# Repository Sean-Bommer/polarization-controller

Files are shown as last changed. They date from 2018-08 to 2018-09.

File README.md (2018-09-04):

# polarization-controller-Unit
Repository for all the final files of the polarization controller project completed by Sean Bommer.

The polarization controller unit (PCU) is a modular laser cut device that is capable of rotating 2 1-inch polarizing waveplates.
it operates using an Arduino Nano and two DRV8834 stepper motor drivers, found at the folowing link.
https://www.pololu.com/product/2134
which control 2 28BYJ-48 5V Stepper Motors.
the construction is made up from 3mm acrylic and M3 bolts and nuts.

The PCU can be powered from the 5V line of the Arduino Nano, which allowing for the whole system to be run from the USB port of a PC.
The OS for the device is contained in the Arduino IDE code in this repository, two versions are available:
  
  The 'position' version sets the start location (it's position when switched on) as position = 0 Degrees and then rotates the waveplate     to  the target orientation with respect to this 0 position. For example, upon start up the device is asked to rotate to 90 degrees. the   device turns to this position. it is then asked to turn to 90 degrees again. the device does not move, as it is already at 90 degrees.
  
  The 'distance' version reads the degrees input as how far it should rotate. For example, upon start up the device is asked to rotate 90   degrees. the device turns this distance. it is then asked to turn 90 degrees again. the device will turn another 90 degrees, thus being   180 degrees from it's origin point.
  
This device is designed to be very modular, and complies to the dimensions required for the Thorlabs cage mount system. the waveplates are controlled independently of each other so it can operate with either one or 2 waveplates. 

When attached to the base mount via the M3 screws the, the whole system can be mounted to an optical breadboard via the 2 slots either side of the base and up to 4 L-shaped mounting brackets. In this configuration, with two waveplates setup, the PCU can serve as a mounting point for a simple optical cage setup as well.

FOLDERS:
        
        The Arduino folder contains the position and distance versions of the OS which are compatible with the arduino Nano.
        it also contains the autostep testscript, that can be used to check if all components work without serial communication and also 
        measure any motor drift the system has when used in conjunction with the Matlab findMotorDrift.m file.
        
        The Matlab folder has the findMotorDrift.m file which can be used to measure the motor drift of the system whn used with the
        autostep arduino script.
        
        The LabVIEW folder holds a simple Serial Interface with the PCU allowing simple click and go operation of the PCU

        The PCB folder has all the Kicad files needed for the design of the PCU PCB on a one-sided copper plate.

        the Fusion 360 contains the design files for the laser cut acrylic parts of the PCU.

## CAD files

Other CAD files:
Fusion360/Driver Gear (hobby) v5.f3d
Fusion360/Lens Holder Cover v5.f3d
Fusion360/Master Base Mount v6.f3d
Fusion360/Master Panels v19.f3d

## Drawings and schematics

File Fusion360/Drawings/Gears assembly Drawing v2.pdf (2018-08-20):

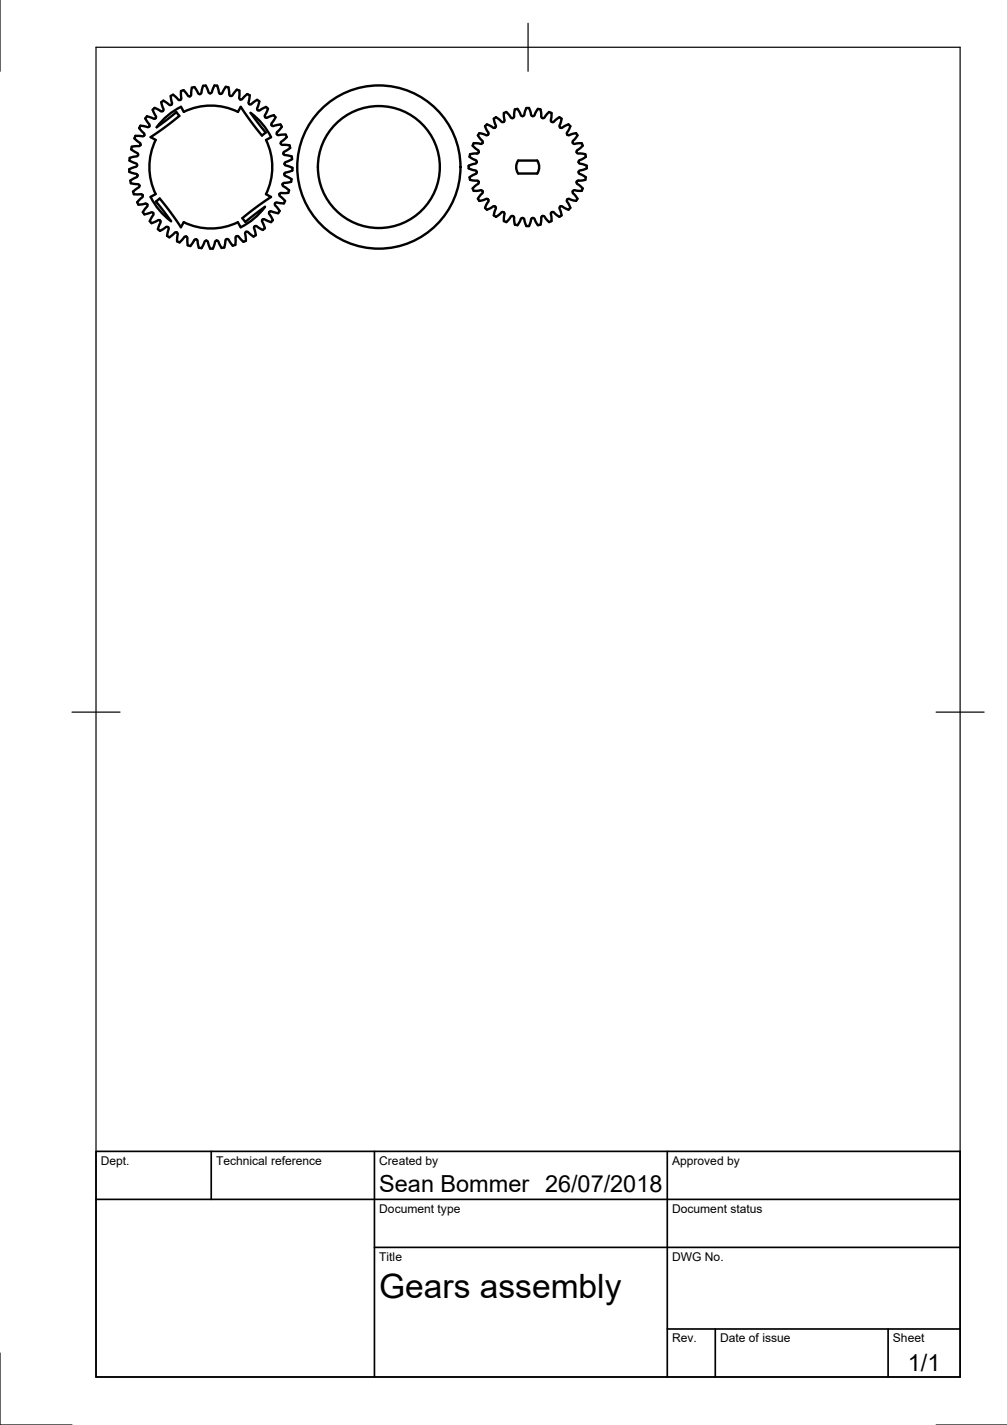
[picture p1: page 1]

Dept. | Technical reference | Created by Sean Bommer 26/07/2018 | Approved by

Document type | Document status

Title Gears assembly | DWG No.

Rev. | Date of issue | Sheet 1/1

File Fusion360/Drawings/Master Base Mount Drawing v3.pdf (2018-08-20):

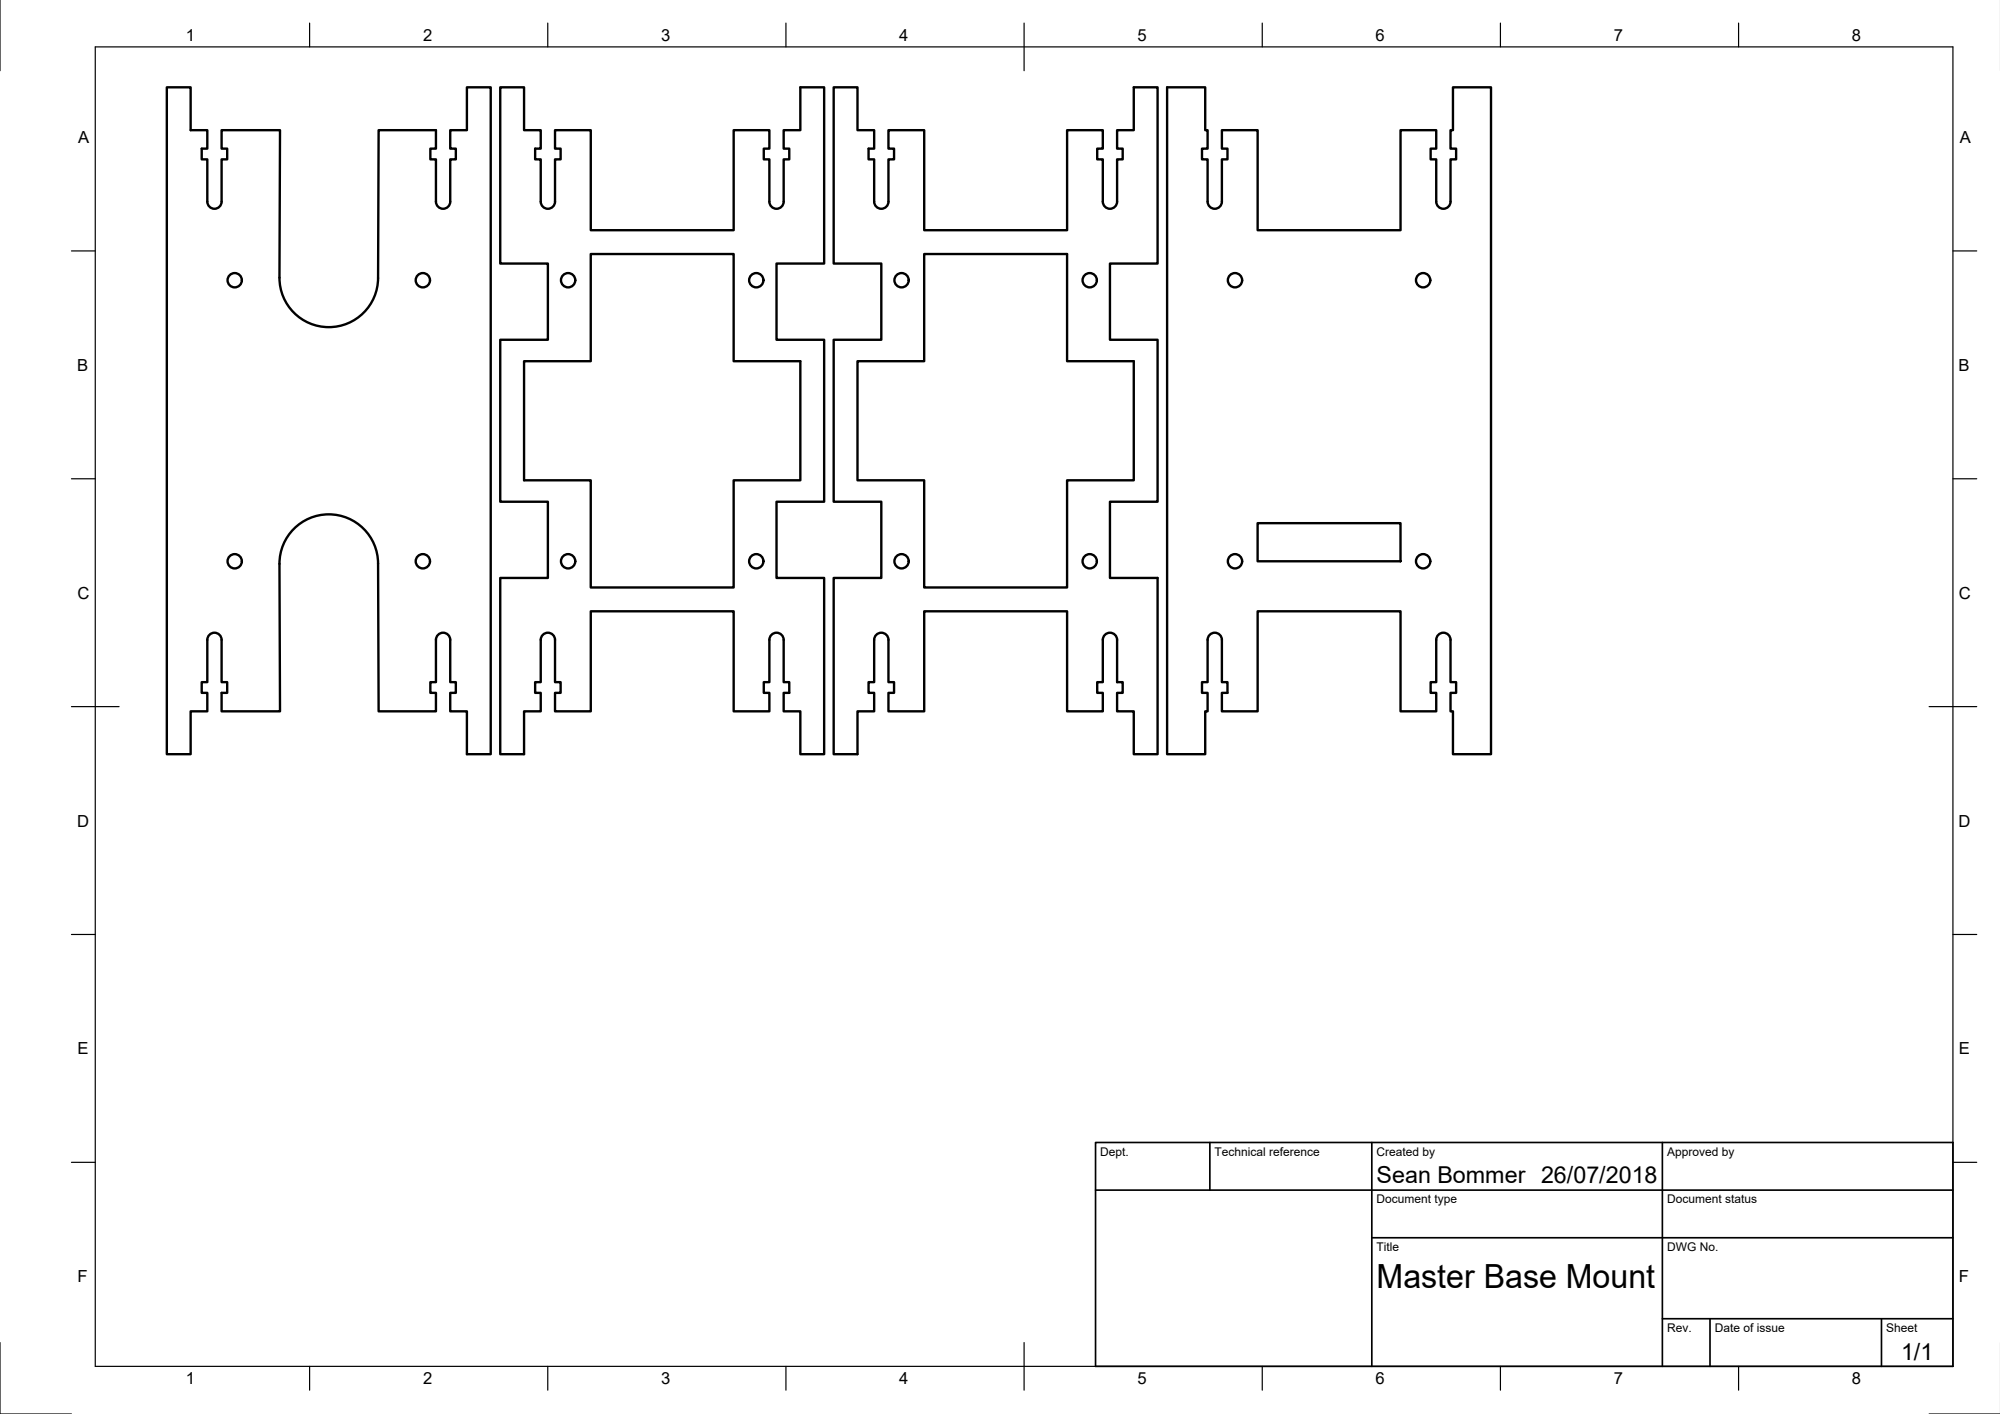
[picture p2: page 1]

Dept. | Technical reference | Created by Sean Bommer 26/07/2018 | Approved by

Document type | Document status

Title Master Base Mount | DWG No.

Rev. | Date of issue | Sheet 1/1

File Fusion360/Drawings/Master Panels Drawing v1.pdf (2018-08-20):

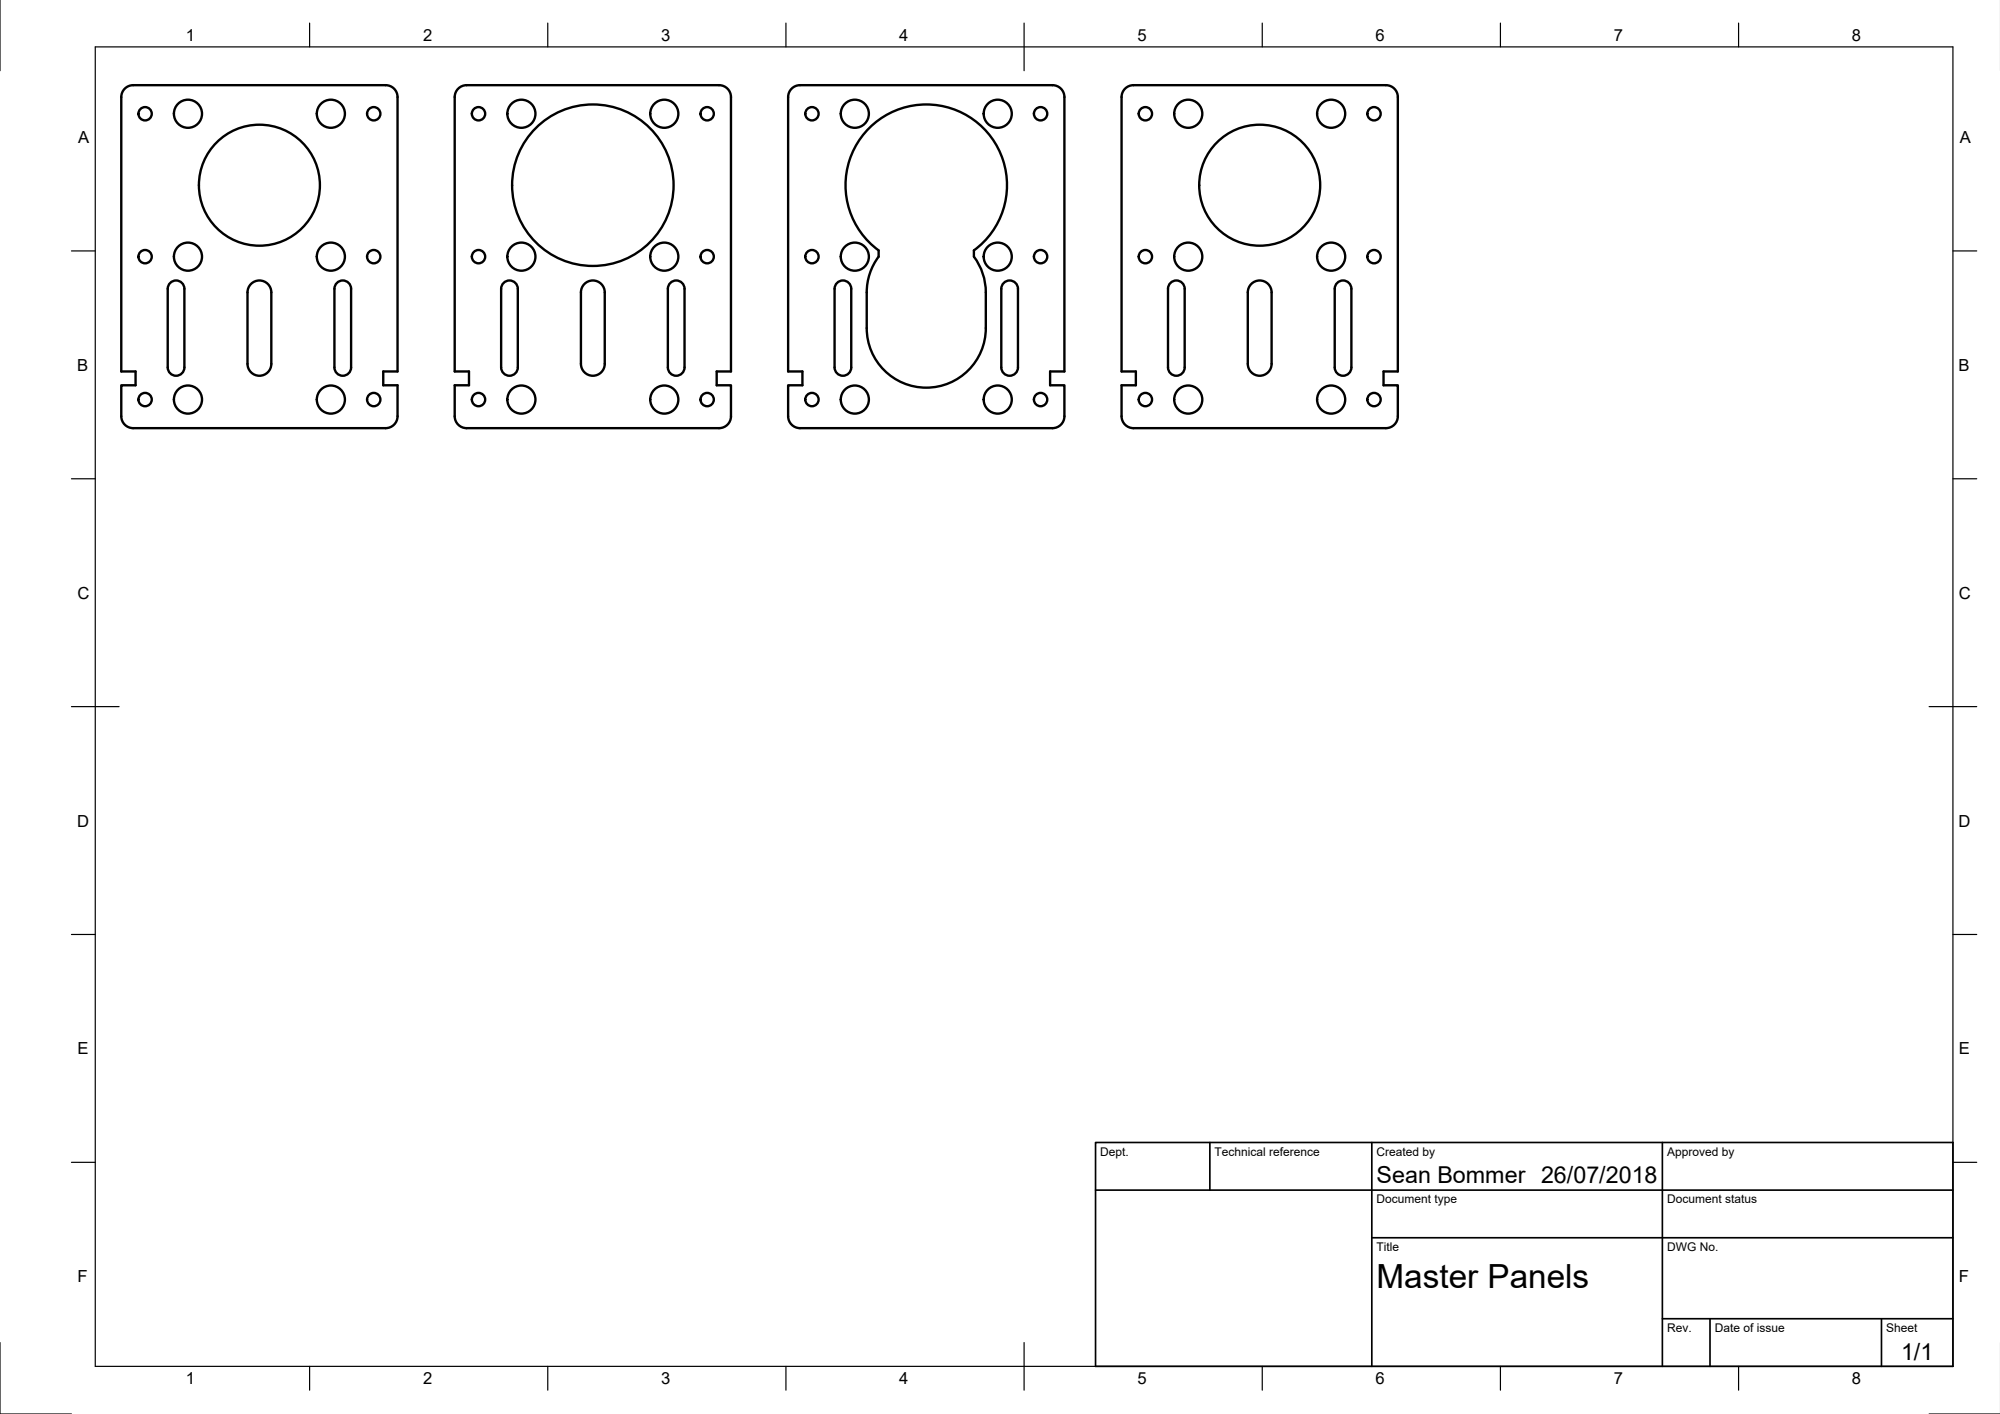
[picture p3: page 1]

Dept. | Technical reference | Created by Sean Bommer 26/07/2018 | Approved by

Document type | Document status

Title Master Panels | DWG No.

Rev. | Date of issue | Sheet 1/1

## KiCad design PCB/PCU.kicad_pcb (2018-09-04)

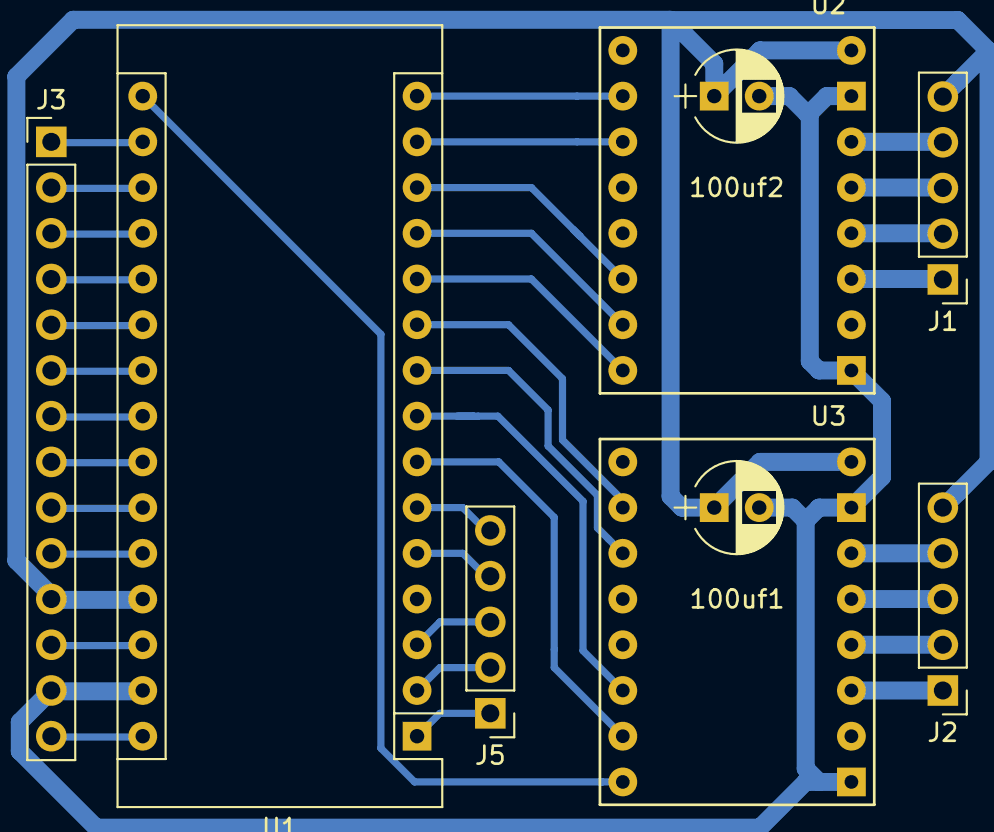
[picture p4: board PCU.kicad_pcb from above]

Board: 2 copper layers, 9 parts (0 on the bottom side), 37 nets.

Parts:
100uf1, 100uf2: CP1; CP_Radial_D5.0mm_P2.50mm
J1, J2, J5: Conn_01x05_Male; Pin_Header_Straight_1x05_Pitch2.54mm
J3: Conn_01x14_Male; Pin_Header_Straight_1x14_Pitch2.54mm
U1: ArduinoNano; Arduino_Nano
U2, U3: DRV8834_LV; drv8834

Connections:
/VMOT: 100uf1.1, 100uf2.1, J1.5, J2.5, J3.11, U1.27, U2.16, U3.16
GND: 100uf1.2, 100uf2.2, J3.13, U1.29, U2.9, U2.15, U3.9, U3.15
unnamed: J1.1, U2.11
unnamed: J1.2, U2.12
unnamed: J1.3, U2.13
unnamed: J1.4, U2.14
unnamed: J2.1, U3.11
unnamed: J2.2, U3.12
unnamed: J2.3, U3.13
unnamed: J2.4, U3.14
unnamed: J3.1, U1.17
unnamed: J3.2, U1.18
unnamed: J3.3, U1.19
unnamed: J3.4, U1.20
unnamed: J3.5, U1.21
unnamed: J3.6, U1.22
unnamed: J3.7, U1.23
unnamed: J3.8, U1.24
unnamed: J3.9, U1.25
unnamed: J3.10, U1.26
unnamed: J3.12, U1.28
unnamed: J3.14, U1.30
unnamed: J5.1, U1.1
unnamed: J5.2, U1.2
unnamed: J5.3, U1.3
unnamed: J5.4, U1.5
unnamed: J5.5, U1.6
unnamed: U1.7, U3.7
unnamed: U1.8, U3.6
unnamed: U1.9, U3.3
unnamed: U1.10, U3.2
unnamed: U1.11, U2.8
unnamed: U1.12, U2.7
unnamed: U1.13, U2.6
unnamed: U1.14, U2.3
unnamed: U1.15, U2.2
unnamed: U1.16, U3.8

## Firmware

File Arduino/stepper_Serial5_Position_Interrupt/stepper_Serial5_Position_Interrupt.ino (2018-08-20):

// incorporate math library that contains advanced math functions
#include <math.h>

// rename pins used for easier coding =======================

byte Dir0 = 4;    byte Dir1 = 9;
byte Step0 = 5;   byte Step1 = 10;
byte m10 = 6;     byte m11 = 11;
byte m00 = 7;     byte m01 = 12;
byte sleep0 = 13;  byte sleep1 = 8;
// initialise motor pins catalog ============================
int motorCatalog[2][5] = {
  {Dir0, Step0, m10, m00, sleep0},
  {Dir1, Step1, m11, m01, sleep1}  
};

// initialise array of movement parameters ==================
float motorMove[2][3] = {};

// initialise array of resolution values ====================
int resArray[6][3] ={
  {1,0,0},{1,1,0},{0,0,0},{1,0,1},{1,1,1},{0,0,1}
};

// csv parameters ===========================================
int motorName; 
int Resolution;   
int Direction;
int Degrees;
int go;  
int stepsToTake;  
float stepsPerDegrees = 8;

// initialise counter variables =============================
long ii = 0;           long jj = 0;
float distanceBetween0 = {};
float distanceBetween1 = {};

//  setup range function ====================================
bool inRange(int val, int minimum, int maximum)
{
  return ((minimum <= val) && (val <= maximum));
}

void setup() { //===========================================================================================
  // initialize the serial port: ============================
  Serial.begin(38400);
  while(!Serial){
    // Prevents other code from running until com port is connected
  }
  Serial.println("begin");
  
  // Define pins used =======================================
  pinMode(sleep0, OUTPUT);
  pinMode(Dir0,OUTPUT);
  pinMode(Step0,OUTPUT);
  pinMode(m10,OUTPUT);
  // pinMode(M00,OUTPUT); needs to swap between input and 
  // output based on loop conditions
  pinMode(sleep1, OUTPUT);
  pinMode(Dir1,OUTPUT);
  pinMode(Step1,OUTPUT);
  pinMode(m11,OUTPUT);
  // pinMode(M01,OUTPUT); needs to swap between input and 
  // output based on loop conditions

  // set current position as origin point ===================
  motorMove[0][0] = 0;
  motorMove[1][0] = 0;

  // setup rotation zero-ing pins ===========================
  pinMode(2, INPUT_PULLUP);
  attachInterrupt(digitalPinToInterrupt(2),zeroM0, RISING);
  pinMode(3, INPUT_PULLUP);
  attachInterrupt(digitalPinToInterrupt(3),zeroM1, RISING);

  // set sleep pins off =====================================
  digitalWrite(sleep0, LOW); // sleeps motor
  digitalWrite(sleep1, LOW); // sleeps motor
}

void loop() { // ============================================================================================
  
  // Have arduino wait to recieve input =====================
  while (Serial.available() > 0){
  
  // Interpret csv serial input =============================
  
  int motorName = Serial.parseInt();
  int Resolution = Serial.parseInt();
  int Direction = Serial.parseInt();
  float Degrees = Serial.parseFloat();
  int go = Serial.parseInt();
  
  // ========================================================
  if (go == 1){ 
  // only runs the following loop if the go condition is met,
  // prevents running when no serial information is given
  
  // ========================================================
  // calculate shortest possible path to take
  // VV reduces the Degrees value to either +/- 180 degrees from current position

  // could possibly be simplified
  
  while (Degrees > 360.0){
    Degrees = Degrees - 360.0;
  }
  if ((Degrees - motorMove[motorName][0]) > 180.0){
    Degrees = (Degrees - 360.0);
  }

  while (Degrees < -360.0){
    Degrees = Degrees + 360.0;
  }
  if ((Degrees - motorMove[motorName][0]) < -180.0){
    Degrees = (Degrees + 360.0);
  }

  float stepsToTake = (Degrees - motorMove[motorName][0])*(stepsPerDegrees);  //how many motor steps per degrees  

  // Calculate other variables ==============================
  float microStep = 1.0/(float)Resolution; // fraction needs to be float
  long microStepsToTake = round(abs(stepsToTake)*Resolution);
  
  // Save to Motor ==========================================
  motorMove[motorName][1] = (float)Resolution;
  motorMove[motorName][2] = (float)Degrees;
    Serial.println(motorMove[motorName][1]);
    Serial.println(motorMove[motorName][2]);
    delay(2000);

  // Check Resolution Conditions ============================
  int Res = log10(Resolution)/log10(2); 
  // ^^ finds the exponent value of 2^n, where n corresponds to a row in resArray
  // vv uses the information in the nth row of resArray to configure the resolution in the stepper board
    pinMode(motorCatalog[motorName][3],resArray[Res][0]);
    digitalWrite(motorCatalog[motorName][3],resArray[Res][1]);
    digitalWrite(motorCatalog[motorName][2],resArray[Res][2]);
    
  // Display motor information ==============================
  
  Serial.print("Moving motor ");
  Serial.print(motorName);
  Serial.print(" to ");
  Serial.print(Degrees);
  Serial.print(" degrees in ");
  Serial.print(microStepsToTake);
  Serial.println(" micro steps");
  }
  }
  // Actually move motor ====================================
    float increment0 = 1.0/(motorMove[0][1]*stepsPerDegrees);
    float increment1 = 1.0/(motorMove[1][1]*stepsPerDegrees);
    
    if (motorMove[0][0] >= motorMove[0][2] + increment0 || motorMove[0][0] <= motorMove[0][2] - increment0){  
      // ^^ compares current position to destination
      distanceBetween0 = motorMove[0][2] - motorMove[0][0];
      digitalWrite(motorCatalog[0][4], 1); // wakes motor
      
      if (distanceBetween0 >= increment0){  // checks if it should be moving clockwise or counter clockwise
        motorMove[0][0] = motorMove[0][0] + increment0;
        // ^^ adds 1 unit of distance to the position, proportional to resolution and steps per degrees
        Serial.println(motorMove[0][0]);
        digitalWrite(motorCatalog[0][0], 0); // sets direction
        digitalWrite(motorCatalog[0][1], 1); // sends pulse to step pin
      }
      else if (distanceBetween0 <= -increment0){  // checks if it should be moving clockwise or counter clockwise
        motorMove[0][0] = motorMove[0][0] - increment0;
        // ^^ subtracts 1 unit of distance to the position, proportional to resolution and steps per degrees
        Serial.println(motorMove[0][0]);
        digitalWrite(motorCatalog[0][0], 1); // sets direction
        digitalWrite(motorCatalog[0][1], 1); // sends pulse to step pin      
      }
    }
     else if (motorMove[0][0] <= motorMove[0][2] + increment0 && motorMove[0][0] >= motorMove[0][2] - increment0){
      digitalWrite(sleep0, LOW); // sleeps motor
    }
    if (motorMove[1][0] >= motorMove[1][2] + increment1 || motorMove[1][0] <= motorMove[1][2] - increment1){
      // ^^ compares current position to destination
      distanceBetween1 = motorMove[1][2] - motorMove[1][0];

      digitalWrite(motorCatalog[1][4], 1); // wakes motor
      if (distanceBetween1 >= increment1){  // checks if it should be moving clockwise or counter clockwise
        motorMove[1][0] = motorMove[1][0] + increment1;
        // ^^ adds 1 unit of distance to the position, proportional to resolution and steps per degrees        
        digitalWrite(motorCatalog[1][0], 0); // sets direction
        digitalWrite(Step1, 1); // sends pulse to step pin
      }
      else if (distanceBetween1 <= -increment1){  // checks if it should be moving clockwise or counter clockwise
        motorMove[1][0] = motorMove[1][0] - increment1;
        // ^^ subtracts 1 unit of distance to the position, proportional to resolution and steps per degrees
        digitalWrite(motorCatalog[1][0], 1); // sets direction
        digitalWrite(Step1, 1); // sends pulse to step pin        
      }
    }
     else if (motorMove[1][0] <= motorMove[1][2] + increment0 && motorMove[1][0] >= motorMove[1][2] - increment0){
      digitalWrite(sleep1, LOW); // sleeps motor
    }
    
  // switch pins off ========================================      
    delay(4);
    digitalWrite(motorCatalog[0][1], LOW);
    digitalWrite(motorCatalog[1][1], LOW);
}

void zeroM0() {
  motorMove[0][0] = 0;
  Serial.println("interrupt");
}
void zeroM1() {
  motorMove[1][0] = 0;
  Serial.println("interrupt");
}

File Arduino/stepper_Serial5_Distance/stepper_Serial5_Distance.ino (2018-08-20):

// incorporate math library that contains advanced math functions
#include <math.h>

// rename pins used for easier coding =======================
byte Dir0 = 4;    byte Dir1 = 9;
byte Step0 = 5;   byte Step1 = 10;
byte m10 = 6;     byte m11 = 11;
byte m00 = 7;     byte m01 = 12;

// initialise motor pins catalog ============================
int motorCatalog[2][4] = {
  {Dir0, Step0, m10, m00},
  {Dir1, Step1, m11, m01}  
};

// initialise array of movement parameters ==================
long motorMove[2][6] = {};

// csv parameters ===========================================
int motorName; 
int Resolution;   
int Direction;
int Degrees;
int go;  
int stepsToTake;  
float stepsPerDegrees = 8;

// initialise counter variables =============================
long ii = 0;           long jj = 0;

// initialise locking variables =============================
//byte lock0 = 0;       byte lock1 = 0;


void setup() { //===========================================================================================
  // initialize the serial port: ============================
  Serial.begin(38400);
  while(!Serial){
    // Prevents other code from running until com port is connected
  }
  Serial.println("begin");
  
  // Define pins used =======================================
  pinMode(Dir0,OUTPUT);
  pinMode(Step0,OUTPUT);
  pinMode(m10,OUTPUT);
  // pinMode(M00,OUTPUT); needs to swap between input and 
  // output based on loop conditions
  pinMode(Dir1,OUTPUT);
  pinMode(Step1,OUTPUT);
  pinMode(m11,OUTPUT);
  // pinMode(M01,OUTPUT); needs to swap between input and 
  // output based on loop conditions
}

void loop() { // ============================================================================================
  
  // Have arduino wait to recieve input =====================
  while (Serial.available() > 0){
  
  // Interpret csv serial input =============================
  
  int motorName = Serial.parseInt();
  int Resolution = Serial.parseInt();
  int Direction = Serial.parseInt();
  float Degrees = Serial.parseFloat();
  int go = Serial.parseInt();

  float stepsToTake = Degrees*(stepsPerDegrees); 
  //how many motor steps per degrees
  
  // Troubleshoot Area ======================================
  //Serial.println(go);
  //Serial.println(motorName);
  //Serial.println(Resolution);
  //Serial.println(Direction);
  //Serial.println(Degrees);    

  // Calculate other variables ==============================
  float microStep = 1.0/(float)Resolution; // fraction needs to be float
  long microStepsToTake = round(abs(stepsToTake)*Resolution);

  // Troubleshoot Area ======================================
  
  //Serial.println(microStep);
  //Serial.println(microStepsToTake);
  
  // Save to Motor ==========================================
  if (go == 1){
    motorMove[motorName][0] = microStepsToTake;
  
  // Check Resolution Conditions ============================
  if (Resolution == 1){
    pinMode(motorCatalog[motorName][3],OUTPUT);
    digitalWrite(motorCatalog[motorName][3],LOW);
    digitalWrite(motorCatalog[motorName][2],LOW);
  }
  else if (Resolution == 2){
    pinMode(motorCatalog[motorName][3],OUTPUT);
    digitalWrite(motorCatalog[motorName][3],HIGH);
    digitalWrite(motorCatalog[motorName][2],LOW);
  }
  else if (Resolution == 4){
    pinMode(motorCatalog[motorName][3],INPUT);
    digitalWrite(motorCatalog[motorName][3],LOW);
    digitalWrite(motorCatalog[motorName][2],LOW);
  }
    else if (Resolution == 8){
    pinMode(motorCatalog[motorName][3],OUTPUT);
    digitalWrite(motorCatalog[motorName][3],LOW);
    digitalWrite(motorCatalog[motorName][2],HIGH);
  }
    else if (Resolution == 16){
    pinMode(motorCatalog[motorName][3],OUTPUT);
    digitalWrite(motorCatalog[motorName][3],HIGH);
    digitalWrite(motorCatalog[motorName][2],HIGH);
  }
    else if (Resolution == 32){
    pinMode(motorCatalog[motorName][3],INPUT);
    digitalWrite(motorCatalog[motorName][3],LOW);
    digitalWrite(motorCatalog[motorName][2],HIGH);
  }
  // Check Direction Conditions =============================
  if (Degrees > 0 && Direction == 0){
    digitalWrite(motorCatalog[motorName][0], LOW);
    //Serial.println(" Condition 1");
  }
  else if (Degrees > 0 && Direction == 1){
    digitalWrite(motorCatalog[motorName][0], HIGH);
    //Serial.println(" Condition 2");
  }
  else if (Degrees < 0 && Direction == 0){
    digitalWrite(motorCatalog[motorName][0], HIGH);
    //Serial.println(" Condition 3");
  }
  else if (Degrees < 0 && Direction == 1){
    digitalWrite(motorCatalog[motorName][0], LOW);
    //Serial.println(" Condition 4");
  }

  // Display motor information ==============================
  Serial.print("Moving motor ");
  Serial.print(motorName);
  Serial.print(" ");
  Serial.print(Degrees);
  Serial.print(" degrees in ");
  Serial.print(microStepsToTake);
  Serial.println(" micro steps");
  }
  }
  // Actually move motor ====================================
    if (ii < motorMove[0][0]){
    digitalWrite(motorCatalog[0][1], HIGH);
    ii = ii+1;
    }
    else if (ii == motorMove[0][0]){
    ii = 0;
    motorMove[0][0] = 0;
    }
    
    if (jj < motorMove[1][0]){
    digitalWrite(motorCatalog[1][1], HIGH);
    jj = jj+1; 
    }
    else if (jj == motorMove[1][0]){
    jj = 0;
    motorMove[1][0] = 0;
    }
  // switch pins off ========================================      
    delay(4);
    digitalWrite(motorCatalog[0][1], LOW);
    digitalWrite(motorCatalog[1][1], LOW);
}

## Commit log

2018-08-20 Add files via upload
    Arduino based OS code for the polarisation controller
2018-09-04 Add files via upload
    Only the relevant KiCad files
    [PCU.kicad_pcb, PCU.sch]
